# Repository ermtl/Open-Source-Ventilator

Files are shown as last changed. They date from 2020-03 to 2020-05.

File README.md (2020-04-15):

# Open-Source-Ventilator

The project now contains a complete functional ventilator (prototype stage) with both the controller, and the complete mechanical design, all the 3D printed parts (both STL & CAD files) as well as the CNC files for the box.

The complete part list will be updated soon.

Video presentation / demo : 

<a href="http://www.youtube.com/watch?feature=player_embedded&v=0-nGLLX1W8E
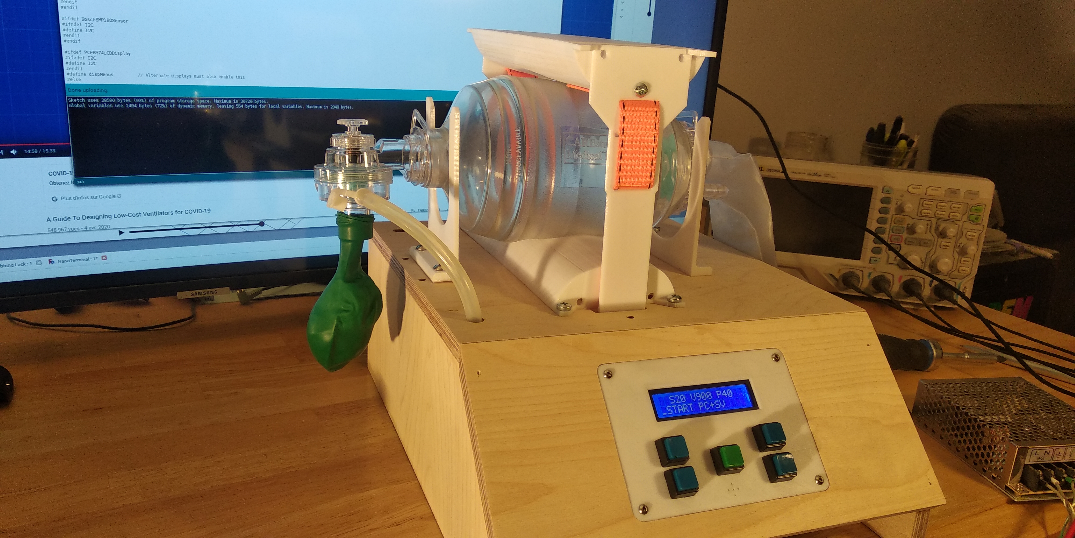
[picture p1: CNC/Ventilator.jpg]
" target="_blank"></a>

The mechanism uses a simple but effective drive mechanism based on a single high strength nylon or polyester webbing strap to squeeze the bag from both sides with minimal mechanical losses.
This design (author unknown) inspired me to explore this solution.

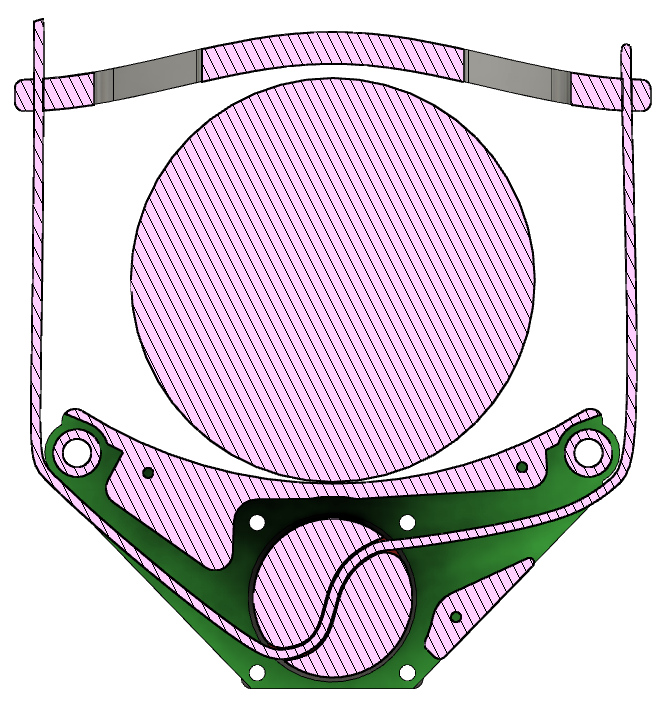
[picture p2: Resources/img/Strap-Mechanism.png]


A major change was to use a much smaller diameter aluminum shaft instead of a drum as this gives the required torque. Also lateral guides are added to ensure a better stability. Also the parts in contact with the BVM are convex instead of being concave as the shape squeezes the BVM in a way that allows to extract more air with minimal force and without damaging the BVM.

The motor is also more powerful than in many other designs I've seen while retaining good position control, allowing it to compress the BVM fast, precisely even at high pressure.

The previously released control software is compatible with this mechanical design and many others.

This software is designed to control a Bag Valve Mask (BVM) AmbuBag medical Ventilator as part of the global effort to develop a fast, effective, easily replicable device using distributed digital manufacturing techniques including 3D printing, CNC or laser cutting. The project uses an Arduino Nano with Atmega328P. The software can be used with a wide range of mechanical designs.

Short video presentation / demo : 

<a href="http://www.youtube.com/watch?feature=player_embedded&v=izh4YnG1fPI
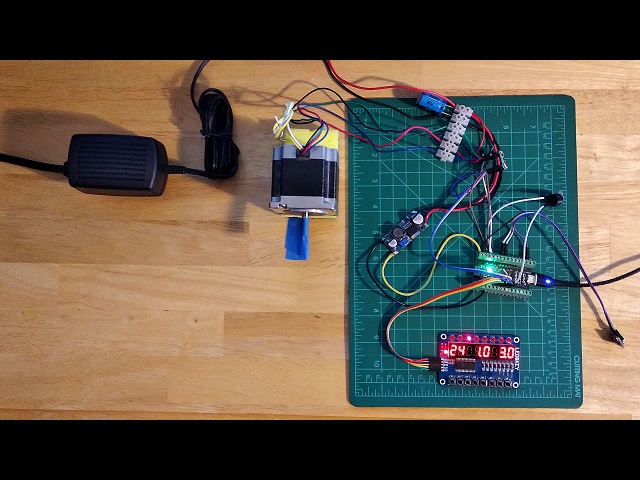
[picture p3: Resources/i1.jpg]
" target="_blank"></a>

(I'm not a youtuber and English's not my main language, you've been warned !)

NOTE: Requirements for a [minimal emergency ventilator device](https://www.gov.uk/government/publications/coronavirus-covid-19-ventilator-supply-specification/rapidly-manufactured-ventilator-system-specification) have been issued by the UK government, and now the WHO as part of a [Disease commodity package](https://www.who.int/publications-detail/disease-commodity-package---novel-coronavirus-(ncov)). This controller strives to follow these guidelines.

Thanks to [uxvrob](https://github.com/uxvrob) we now have a [complete schematic diagram](https://github.com/ermtl/Open-Source-Ventilator/blob/master/hardware/OpenSourceVentilator_sch.pdf) so that the controller can be tested.

As of V0.20, the controller now outputs data that can use an external HMI or the Arduino plotter to output realtime data. Actual plot below (the pink pressure trace was generated by manually pressing an ambu-bag. The right of the screen shows a pressure limited cycle).

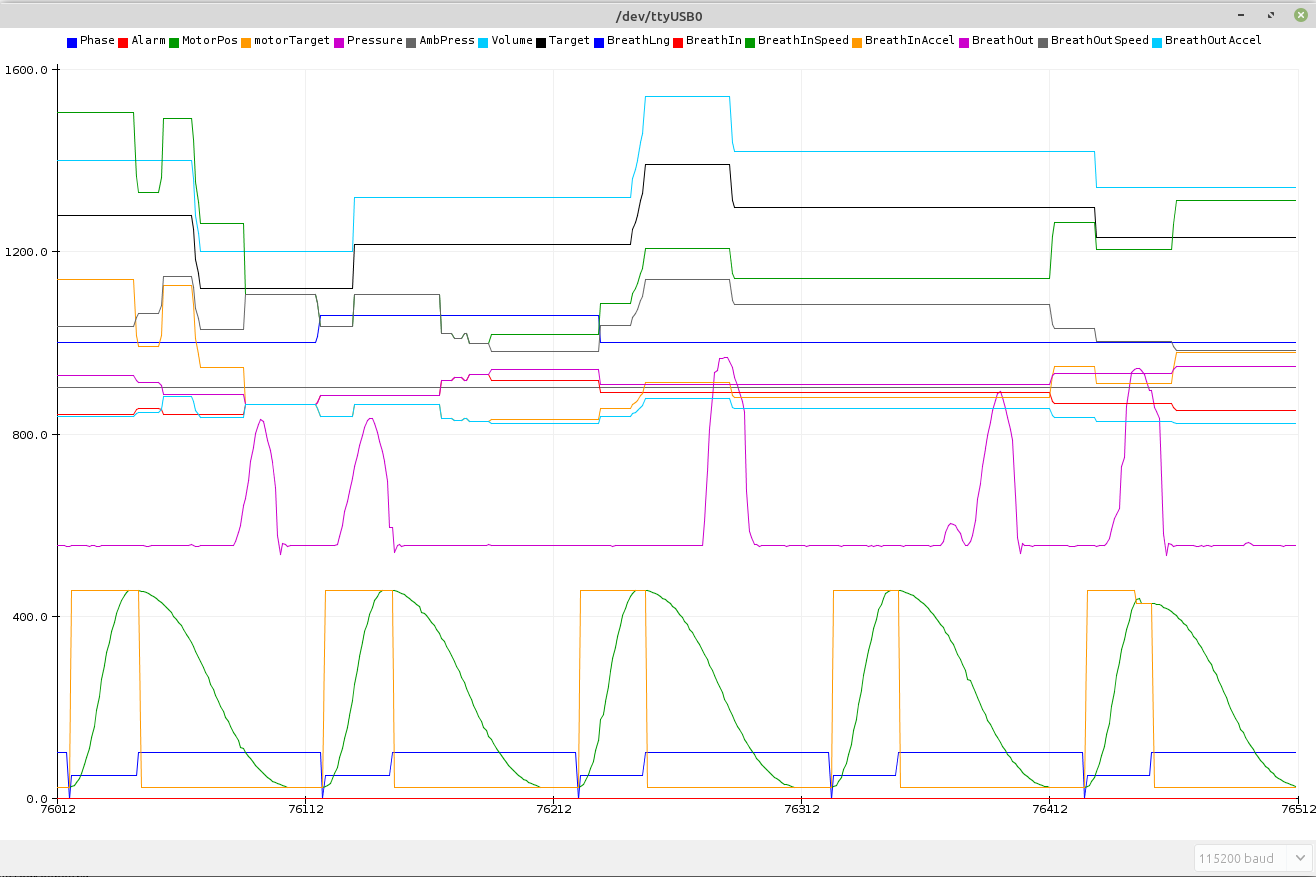
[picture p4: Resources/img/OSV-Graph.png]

 
 (release notes are at the end)

# Main components

- The arduino Nano was chosen as a controller for it's ability to perform the realtime tasks with relatively low latency (step generation & data acquisition) and it's universal availability. More sophisticated controllers such as the Raspberry Pi usually have real time issues and unpredictable latency. Also, the Arduino ecosystem is very rich in well tested libraries.

- The Bosch Sensortech BME280 / BMP280 sensor allows precise measurement of the air pressure delivered to the patient. It also allows measurement of the temperature and pressure (BME280 only). The software allows to use either of these. It'a a well known, mass produced, low cost sensor. 
https://www.bosch-sensortec.com/products/environmental-sensors/humidity-sensors-bme280/

- The TM1638 display / LED / keyboard
This little board merges leds, a 8 digits 7 segments display and 8 buttons. It's a very common Chinese board that possesses numerous advantages. It's main drawback is the Old School look of it's display, but does it really matter for this usage ?
The main advantages are that the board is mechanically integrated making mechanical assembly very easy. Connection to the processor uses only 3 pins (Data, Clock, Strobe) The data is clocked and not timing sensitive. The whole board typically costs 1.50$
2x16 character LCDs require a lot of pin connections or, when used with a "backpack", they require a serial interface. Also, the LCD needs a temperature dependant analog adjustment to be well readable. The display is not very bright and can't be read from a distance. That could be a problem when a person has to monitor several heavily infected patients. They also require a separate keyboard. OLED displays are not suited for this device as their active lifetime is limited. color LCDs would be another possibility, possibly with a touchscreen, but it would take longer to develop and require a more powerful processor without adding much to the main function of the device.

- StepStick stepper driver
The stepstick stepper motor drivers are widely available as they are used to drive 3D printer motors.
When used with 24V and a low current/high torque NEMA23 motor, they can offer a very good torque. There are several types depending on the chip they use (A4988 / DRV8825 / Trinamic TMC2209 & TMC5160). The TMC5160 drives up to 4.4Amps and is even suitable for a NEMA24 or NEMA34 motor. All Trinamic drivers include advanced functions such as load  measurement, stall prevention and detection, noiseless operation, etc ...
https://www.trinamic.com/products/integrated-circuits/
Since the software uses industry standard STEP/DIR interface, any external driver may be used to control a stepper, a servo-stepper or a 3 phases servo. A servo would probably be required for a leadscrew design, while a stepper would be more suited to a direct drive design.

To compile the software, you will need the following libraries (all from the library manager) :
```
#include <BME280I2C.h>             // Temperature / humidity / pressure
                                   //  by Tyler Glenn - https://github.com/finitespace/BME280
#include <Wire.h>                  // I2C protocol
#include <EEPROM.h>                // read / write to the processor's internal EEPROM
#include <TM1638plus.h>            // Keyboard / display / LED combo board
                                   //  By Gavin Lyons - https://github.com/gavinlyonsrepo/TM1638plus
#include <AccelStepper.h>          // Stepper / servo library with step pulse / dir interface
                                   //  By Mike McCauley - http://www.airspayce.com/mikem/arduino/AccelStepper
#include "TimerOne.h"              // Timer component
                                   //  By Jesse Tane, Jérôme Despatis, Michael Polli, Dan Clemens, Paul Stroffregen
                                   //  https://playground.arduino.cc/Code/Timer1/
#include <LiquidCrystal_PCF8574.h> // LCD with PCF8574 "backpack"
                                   //  Matthias Hertel - http://www.mathertel.de/Arduino/LiquidCrystal_PCF8574.aspx 
```
# Software Functions

The software is contained in an Arduino "sketch" with many comments, nearly all parameters are in defined constants and can be easily changed. It is herein distributed under the GPL V3.0 licence. The software has the following functions:

- Initialisation with display keyboard and sensor detection.
The software have been designed to allow operation in degraded mode without BME/BMP280 sensor and even without keyboard / display (it will autostart with stored parameters)
During the startup process, detailed debug information is provided through the serial/USB port. 
TBD : remote operation controlled by USB

- User interface
The software manages the display, keyboard navigation in the settings menu and an alarm beeper.
The 8 leds above the keyboard are used as a bar-graph of the measured pressure and a breath cycle indicator.
The 3rd LED represent neutral atmospheric pressure and blinks at the start of each breathing cycle. 1st and 2nd LEDs on the left indicate a low pressure, those on the right indicate a higher pressure. Display is scaled according to the preset pressure.
The menu allows to change the following parameters:

 - Pulse rate
 The pulse rate in breathing cycles per second can be adjusted between 5 and 60 BPM.

 - Breathing volume
 The breathing volume in liter per cycle can be adjusted between 0.1l and 2l. The motor travel and acceleration are changed according to this parameter. There is a yet to be determined limit for high volume at high pulse rate depending on the mechanical design.
 
 - Breathing Pressure 
 The breathing pressure in KPa can be adjusted between 3Kpa and 30Kpa.
The pressure is used to limit the motor speed / travel to prevent exceeding the preset value.
TBD : This feature is not fully implemented yet (but measurements are available and the stepper library allows to alter the motor parameters while it's rotating).
 
 - Save settings
This saves the 3 settings above  and the running state, thus allowing for automatic start upon powerup.

The user interface management is done in a timed interrupt to be responsive and remain functionnal at all times, so that all parameters can be visualised and changed while the device is operating.

When changing the settings, the change will be gradual with each subsequent breath cycle to prevent sudden changes. The variation speed can be defined for all parameters.

- data acquisition.
Data is acquired from the BME/BMP280 sensor every 100ms. the acquisition includes filtering of the pressure 

# Schematic 

<object data="OpenSourceVentilator/OpenSourceVentilator_sch.pdf" type="application/pdf" width="50%" height="50%">
<embed src="OpenSourceVentilator/OpenSourceVentilator_sch.pdf">
<p>This browser does not support PDFs. Please download the PDF to view it: <a href="OpenSourceVentilator/OpenSourceVentilator_sch.pdf">"Download Schematic</a></p> 
</embed>
</object>

# Required hardware

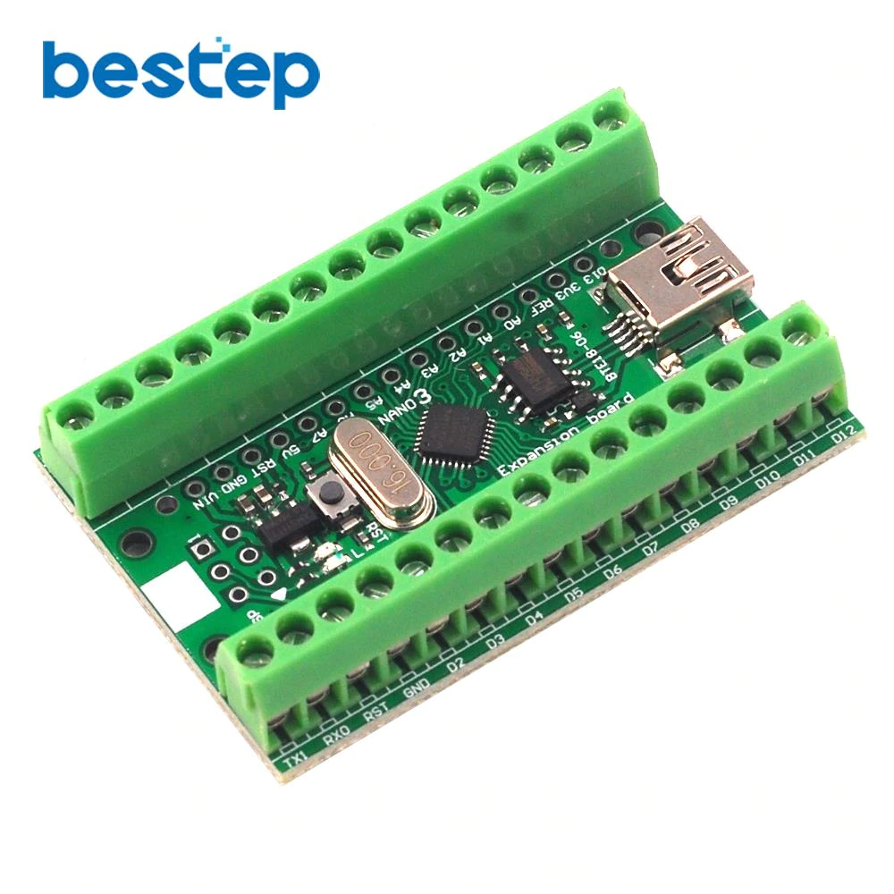
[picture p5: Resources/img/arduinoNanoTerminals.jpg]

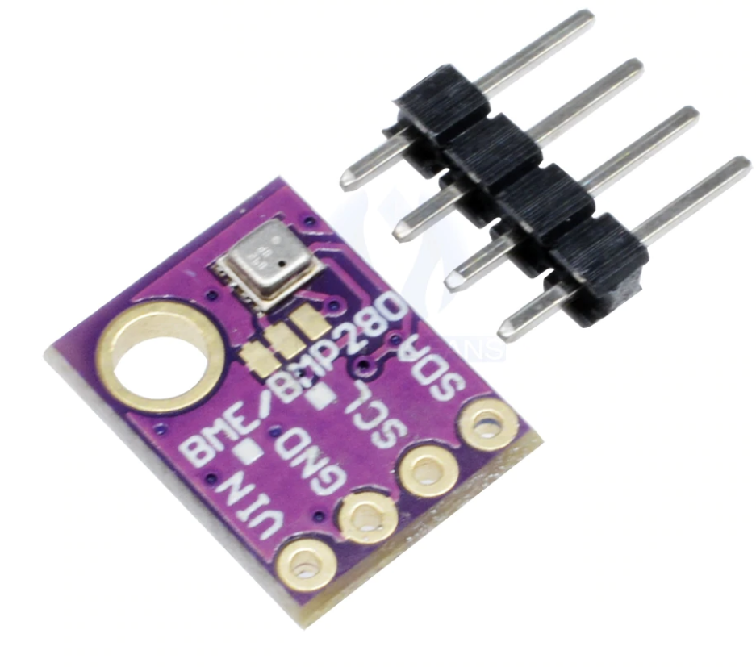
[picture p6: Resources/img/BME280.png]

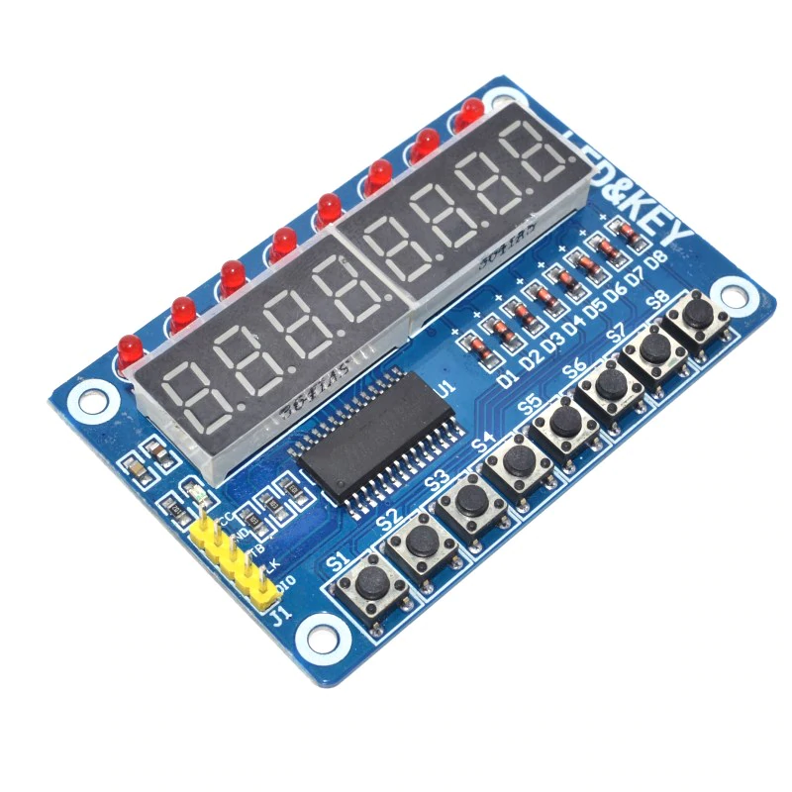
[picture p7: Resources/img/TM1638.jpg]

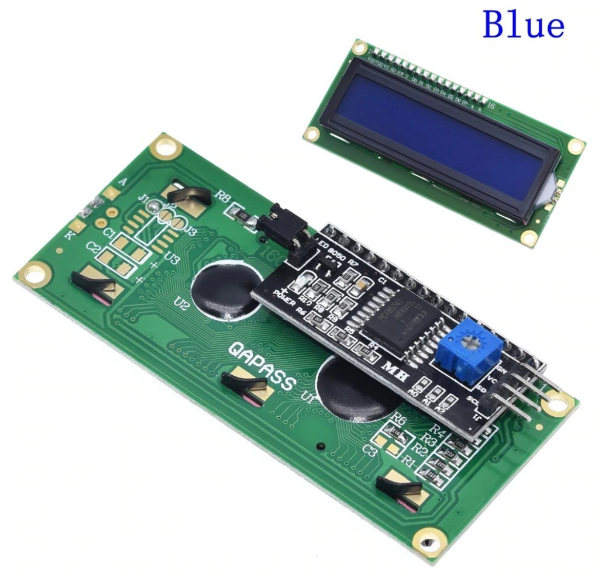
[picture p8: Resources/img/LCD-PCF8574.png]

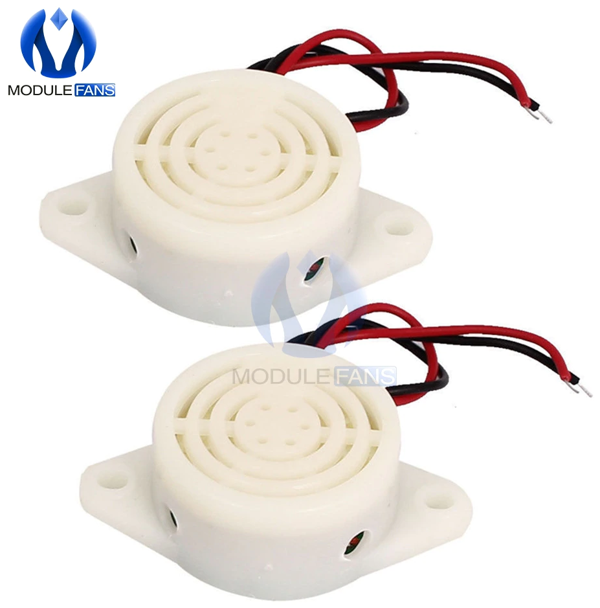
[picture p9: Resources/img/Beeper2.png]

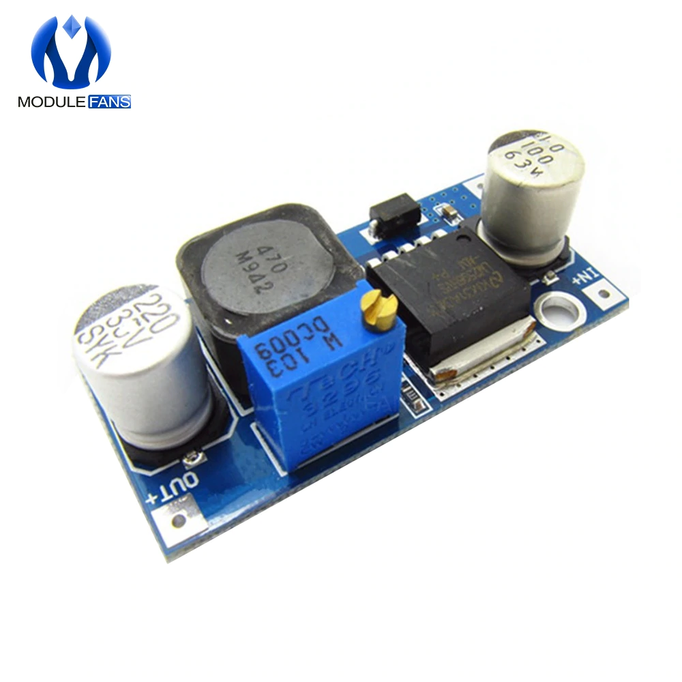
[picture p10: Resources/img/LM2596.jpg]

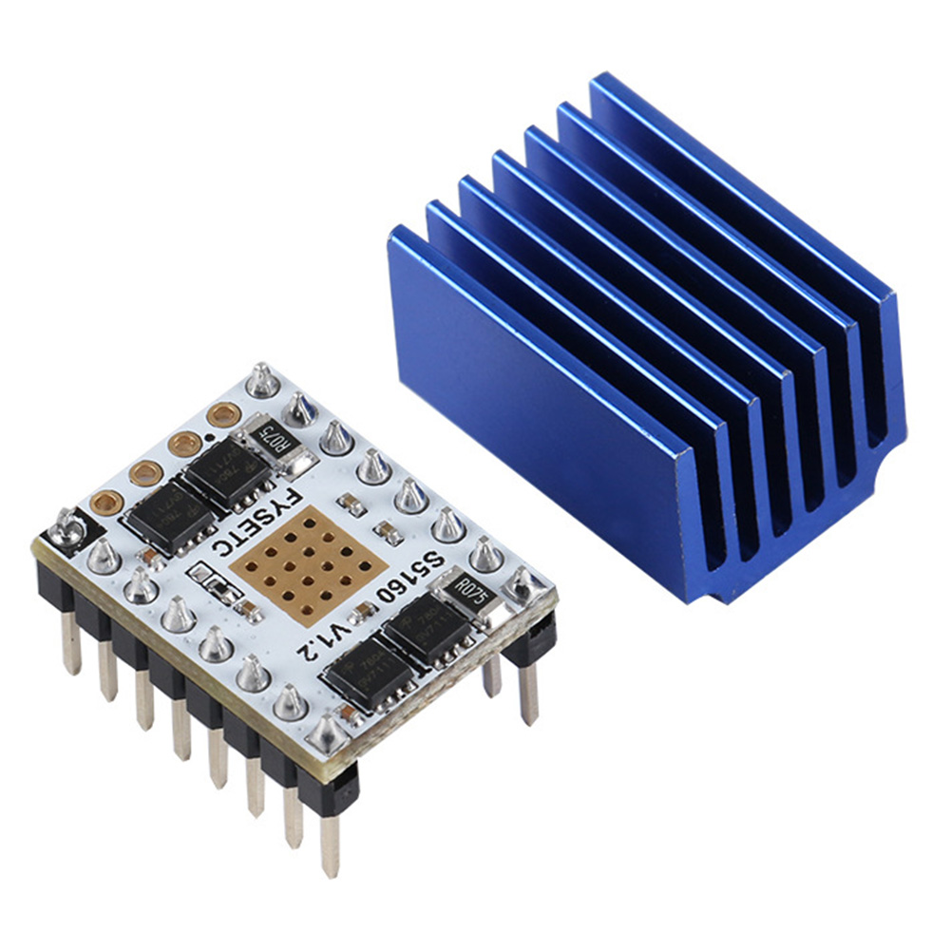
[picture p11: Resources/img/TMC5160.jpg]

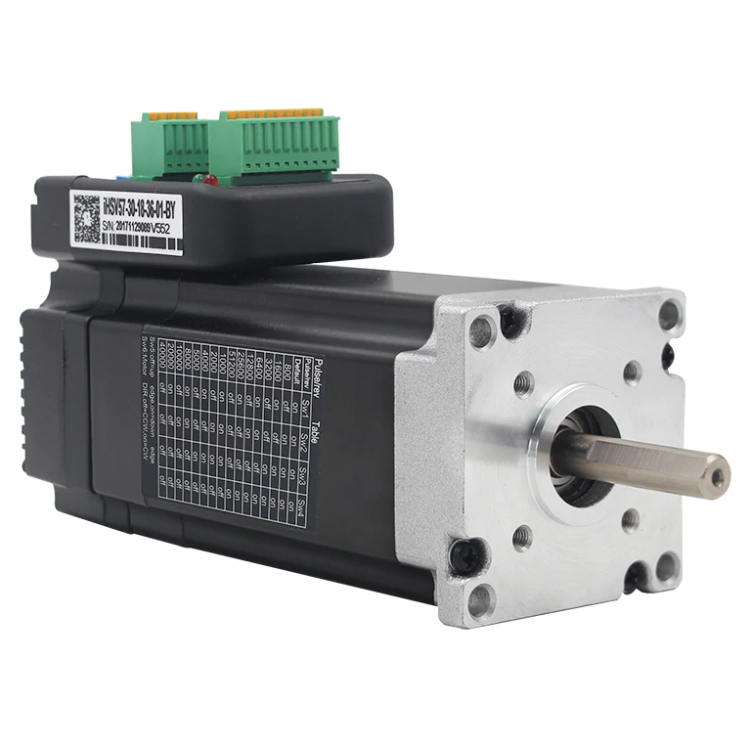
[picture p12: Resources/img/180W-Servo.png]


- Arduino Nano
  Any arduino Nano or clone can be used, as long as it contains an Atmega328 processor
  https://www.aliexpress.com/item/32845440152.html
- Bosch Sensortech BME280 / BMP280 sensor breakout
  Warning, there are 3.3V breakout and 5V breakout boards. Some have 4 pins, others 6 pins.
  They can all be used. Connect the supply accordingly, the 2 extra pins are unused (SPI)
  https://www.aliexpress.com/item/32672562548.html
- TM1638 Display / Leds / Keyboard combo module
  They all have the pin header on top, you can remove the plastic part and bend the pin for side connection
  There are other types of boards with TM1638 chip with 16 buttons, but they lack the LEDs that are important to monitor air pressure measurement.
  https://www.aliexpress.com/item/32807348409.html
- HD44780 With PCF8574 2 lines x 16 character LCD with I2C interface
  These are standard LCD display, and the I2C interface (PCF8574) allows them to be used without taking up many I/O pins.
  https://www.aliexpress.com/item/32651314933.html
- Beeper
  This active beeper is easy to drive and the sound level is mild. 
  https://www.aliexpress.com/item/1893768547.html
  Here is a louder one.
  https://www.aliexpress.com/item/32671465979.html
- Regulator
  Even at 12V, the motor can generate spikes that will damage the controller's regulator. 
  These regulators are cheap, and rated for high voltage (max 50V). 
  The potentiometer needs to be adjusted for 7.5V to 8V
  https://www.aliexpress.com/item/1859113573.html
- Driver and motor.
  The driver and motor required will depend on the mechanical design used.
  here are a few :
  Cheapest, but rugged A4988 Stepstick:
  https://www.aliexpress.com/item/1851964212.html
  DRV8825 StepStick
  https://www.aliexpress.com/item/1937880897.html
  TMC2209 StepStick (silent, with torque detection). 
  Could approximate a pressure measurement for a setup without pressure sensor.
  https://www.aliexpress.com/item/33029587820.html
  TMC5160 StepStick (by far the best option, 4.4A/phase, can drive NEMA34 steppers)
  https://www.aliexpress.com/item/33051621409.html
  As latest calculations ans experimental setups indicate the need for a more powerful
  motor, a LeadShine DM542S (50V 5A seems necessary.
  https://www.aliexpress.com/item/32953743944.html

  For direct drive, a large Nema23 motor with low current and high torque would be best. 
  these motors quickly lose torque as their speed increases, but in this application, 
  their performance should be a good match.
  This one is rated for 1.9NM with only 2.12A (bipolar mode)
  https://www.aliexpress.com/item/4000032106569.html

  For designs using a ballscrew, a servomotor is required to get the necessary speed.
  Here is a good, not too expensive option with integrated controller:
  180W 3000 RPM version https://www.aliexpress.com/item/4000333220649.html
  100W 3000 RPM version https://www.aliexpress.com/item/32945533935.html

# versions

  - 0.10 Initial public version
  
  - 0.11 Add interactive terminal command line complete control (through USB link)
         A minimal device without screen or keyboard is possible with the same software.

  - 0.12 Add "Assist Control" mode with adaptive negative pressure trigger cycle.
This mode was requested by a MD : ```"ER doc here chiming in, hopefully I can answers some questions or clarify minimal requirements.The basic mode you need is Assist Control. This mode provides a breath whenever the patient triggers a breath (by inhaling and creating negative pressure past a certain threshold) or whenever the patient is due for a breath (based on the set rate). The breath it provides are either a fixed volume (and the doc monitors the pressures delivered) or a fixed pressure (and the doc monitors the volume delivered). AC/volume is often called Volume Control, and AC/pressure is often called Pressure Control. While I do not have direct experience ventilating COVID patients yet, these 2 modes will cover 99% of ICU cases."``` 
This version also adds editing, permanent storage and USB setting of the new Patient Synchronization parameter and an audible alarm when pressure remains above 120% of preset pressure for 1 second or mode.
         
  - V0.13 Modular code - asymmetric breathing - Bug fix
This version is a major reorganization of the code done to get a more modular software, ready for bringing in other sensors, a different user interface and ports to other controller architectures. Very long functions are broken down into smaller functionnal blocks that should be much easier to understand and modify, each global variable is commented.
This version also implements most of the guidelines in the UK [minimal emergency ventilator device](https://www.gov.uk/government/publications/coronavirus-covid-19-ventilator-supply-specification/rapidly-manufactured-ventilator-system-specification) specifications. Namely, all variable limits have been tweaked and the variable Inspiratory:Expiratory ratio is fully functionnal.
A bug that allowed floating point variables retrieved from a garbage filled EEPROM to bypass the checks leading to malfunction have been corrected (NaN detection).

  - 0.14 This version include proper timing, speed and acceleration for the motor control.
         The pressure controlled and volume controlled modes are implemented.
         
  - 0.15 Minor version change.
         This version allows the replacement of the buggy Wire.h arduino library  (can hang
         the controller) with a correct version known as jm_Wire
         https://github.com/ermtl/Open-Source-Ventilator/blob/master/OpenSourceVentilator/README.md
         'Wire.h' is still the default library to prevent compiler errors.
         The processor's hardware watchdog can now be enabled (off by default, use with care, you
         risk bricking your processor. 
         Modularisation is getting better (work in progress)         
   
  - 0.16 Double pressure sensor, breath phases modularization
         This version can use 2 absolute sensors (or still use just 1, configurable) to
         constantly monitor the ambiant air pressure. This is important for patients that 
         are heliported and for patients placed in a negative pressure room, 2 situations
         where the ambiant pressure can change rapidly.
         The 2 sensors together will behave as a differential pressure sensor.
         Since pressure is a critical data, several safeguards and coping strategies have 
         been added to make sure data from the sensor is acurate and there is a failsafe.
         Things such as randomly connecting/disconnecting sensors are non blocking and behave 
         as expected.
         this feature requires the #define jm_Wire to be uncommented.Please see the link in
         the description for version 0.15 above

         Also, as requested, the various phases and functions managing the breathing cycle 
         itself have been modularized to allow third parties to implement more sophisticated
         control strategies.

         Finally, the processor's program memory is filing up quickly as the control becomes 
         more complex. There is still opportunities for important optimizations, but the base 
         version will have to give up some non essential functions to fit in a regular Arduino
         Nano (such as the verbose serial interface or the ability to manage both the native
         keyboard / display and the USB serial command line interface.

         This version barely fits with the USB commands on, so they've been deactivated.
         You can get them back by uncommenting the #define USBcontrol line.

         The following versions will both target the Nano and the Mega with Atmega2560 processor
         for 8 times the available program memory.
 
 - 0.17 2x16 LCD Display - Telemetry
       
         The ability to use an alphanumeric 2 lines * 16 characters LCD display had been
         requested, it will now be fully supported. Since this LCD uses lots of IO pins, 
         the retained version is connected to a PCF8574 "Backpack" board to make it I2C 
         compatible. The LCD+the backpack are sold online for around 2.50$.
         The TM1638 display is still supported as a minimal option.
         A good side effect is that the library is lean and so USB/serial terminal control
         is back by default.
         At this point, the keyboard and bargraph are still done with the TM1638, but a
         simple button keyboard will be supported very soon.
         Telemetry will send information in real time about the breathing cycle for further 
         data analysis and / or graphical display !
         This will be very very useful for people developing mechanical solutions, and 
         doing data analysis to develop motor position <=> volume mapping
         Data is sent in common CSV format, around 1 data point every 20 millisecond
         The "T" command, sent through the serial port toggles telemetry on or off.

         every data point includes :
         - Time since the breathing was activated.
         - Breathing cycle phase (more phases might be added in the future)
           0 : Start of new cycle
           1 : Inspiration
           2 : Start of expiration
           3 : Expiration
           4 : Patient breathing initiation search
           5 : Patient initiated a breathing cycle
          - Motor position (in step) Travelled distance depends on driver microstepping
                                     and driving mechanism.
          - relative pressure in cm H2O
         
         In addition to these data points, during phase 0 (start of cycle), the following 
          cycle data is sent:
          - Ambiant pressure (mBar)
          - Breathing volume per cycle in ml
          - Motor destination / target (steps)
          - Breathing length (in seconds)
          - Breathing in duration (in seconds)
          - breathing in top speed (in steps/second)
          - Motor acceleration during inspiration (in steps per second squared)
          - Breathing out duration (in seconds)
          - breathing out top speed (in steps/second)
          - Motor acceleration during expiration (in steps per second squared)
          
    0.20 Realtime graphics, Keyboard, trajectory
         
         This version adds realtime graphics, compatible with the Arduino serial plotter.
         This is an extension of the telemetry in Version 0.17, completed and scaled properly
         for display.
         It shows 2 series of values. The first is updated in realtime (every 20ms) and shows 
         the breathing cycle itself, the commanded motor position, it's actual movement, the 
         pressure sensor output and alarm number.
         The second set is updated once per cycle and shows various values linked to timing, 
         speed, acceleration for various parts of the cycle.
         This data should be extremely useful for developping mechanical prototypes and shows
         the ability to use a remote HMI if desired.
         define ArduinoPlotter for proper visualisation scaling, comment it for real telemetry data 
         This version also add a keyboard as an alternative to the TM1638 keyboard.
         The keyboard used is made with 5 buttons all connected to a single analog input for
         simpler cabling and preserving controller pins.
         https://electronics.stackexchange.com/questions/101409/how-to-debouce-six-buttons-on-one-analog-pin-with-arduino
         The keyboard I use have the following values:
         - 10K to ground
         - 'Enter' button connected to +5V
         - 'Prev'  button connected with a 22Ko resistor
         - 'Next'  button connected with a 10Ko resistor
         - 'Up'    button connected with a 3.6Ko resistor
         - 'Down'  button connected with a 1Ko resistor
         The resulting analog values are stored in the KbdVals[] array, and value tolerance in KbdTols[] array
         If you use different resistor values, uncomment debugAnalogKeyboard to get the analog values to fill the 
         array values.
         Please note that when plotting the graph, while the controller would accept serial data input,the arduino plotter 
         does not allow it, so data needs to be changed using the physical keyboard.
         A 3D printed faceplate containing the display, the buttons and the buzzer is available (including FreeCAD drawing)
         in the 3D-Print directory .
         While graphing the data, a few corrections were made to the trajectory engine.    

    0.21 Pressure unit converted to cm H2O / minor changes
         
         - This version implements the requested change in pressure units as the medical community uses cm H2O and the sensors use Pa.
         - The 'Up' and 'Down' keys now have an auto repeat.
         - When the ventilator is active and 'Enter' is used to stop it, the key press must be pressed 2 seconds and an alarm is sounded.
         - The data dispay includes ambiant pressure (can be used to check negative pressure rooms)
         - It now uses the updated TM1638 library (Version 1.4+), you need to update or you'll have a compile error.
         - #define I2CCheck : displays a list of the I2C devices found upon startup (only for debug or for external HMI)

    0.22 Misc. changes

         - PEEP parameter added
         - Apnea alarm parameter added
         - Display PIP and PEEP in real time (in progress)
         - The bargraph (pressure in VC mode, volume in PC mode) is now displayed on the LCD
         - New automatic motor speed limit to prevent interrupt overflow (interrupt limited reentrancy)
         - reorganisation of items stored in EEPROM. They are now included in a struct and their name starts with ee.
           This will allow easy expansion of the variables stored in EEPROM and the way to treat them as a whole.
         
    0.23 Bug fix with TM1638 display
         When using TM1638 for the display, the menu was broken and displayed an error message.
         
    0.3 Complete ventilator release with plans, 3D prints and CNC 
    
         Complete ventilator release with plans, CAD for 3D prints and CNC
         non linear relation between air volume and motor target position (allows for better adaptation to various non linear   
         mechanisms).
         defining debug_6 allows to check the raw / translated values.
         fix for HD44780 occasionnal display garbling (I2C bus error recovery), requires patched LiquidCrystal_PCF8574 library
         fix for AccelStepper library being too slow to drive microstepped motors, requires patched AccelStepper library
         there is now a separate "OpenSourceVentilator.h" file that contains OEM parameters. 
         This prevents custom changes from being reverted with each new version.
         First version of proportional pressure control  
         Now displays actual volume + actual BPM while breathing
         bug fixes in EEPROM save and restore functions
         bug fix for a mistake that delayed breathing restart
         use of function and unsigned long to prevent millis() rollover problems
         
         thanks to anyone who submitted a bug report!

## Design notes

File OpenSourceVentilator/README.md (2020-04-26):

# Important Note 
about I2C sensors and peripherals using the Arduino Wire.h library

If you compile with any I2C sensor or peripheral that uses the standard Arduino "Wire.h" library, you must be aware that this library is flawed and does contain an infinite loop that will hang the Arduino if an I2C peripheral fails to respond. The only way to exit is to reset it either manually, or using a watchdog. That's been documented since 2011 but Arduino refuses to accept the pull that would correct the situation.

Here are the lines that create the problem (in Wire/utility/twi.c) :

```
// wait for read operation to complete
while(TWI_MRX == twi_state){
continue;
}
```

This case is not supposed to happen according to the I2C protocol, but electrical glitches didn't get the memo. 

Since reliability is paramount in OpenSourceVentilator, the default "Wire.h" library can be switched for the "jm_Wire.h" library that corrects the flaw with a timeout.

However, all libraries that use "Wire.h" will reference it by name in their code, thus a function with the same name will appear to be defined twice, so the compiler will complain loudly and fail.

The solution is to replace the following line in all the library files that contains it.

```
  #include <Wire.h> 
```
with this little preprocessor code
```
  #if __has_include("jm_Wire.h")
  #include <jm_Wire.h>
  #else
  #include <Wire.h>
  #endif
```

That way, the library will use "jm_Wire.h" if it's included in the main program and "Wire.h" otherwise.
You will sometimes need to exit Arduino and restart it for the change to be effective. Unfortunately, if you upgrade a library, you'll have to do the changes all over again. If you know of a better way, please let me know.

here is a list of the libraries used by OpenSourceVentilator and the files that need to be modified:

 - "BME280I2C.h" (pressure / temperature / humidity sensor)
 
   File /libraries/BME280/src/BME280.cpp
 
   File /libraries/BME280/src/BME280I2C.cpp

 - "BMP180MI" (pressure sensor)
 
   File /libraries/BMP180MI/src/BMP180TwoWire.h
   
 - "LiquidCrystal_PCF8574"  (2x16 characters LCD with a PCF8574 "backpack")
 
   File /libraries/LiquidCrystal_PCF8574/src/LiquidCrystal_PCF8574.cpp
 
 - "Adafruit_MPRLS_Library" (pressure sensor)

   File /libraries/Adafruit_MPRLS_Library/Adafruit_MPRLS.cpp

   File /libraries/Adafruit_MPRLS_Library/Adafruit_MPRLS.h

 - "LiquidCrystal_I2C" (various LCD character displays)

   File /libraries/LiquidCrystal_I2C/LiquidCrystal_I2C.cpp
   
   File /libraries/LiquidCrystal_I2C/LiquidCrystal_I2C.h

As I become aware of other libraries used in the project, they will be added to this list.

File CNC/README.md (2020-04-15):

Box-1.DXF contains the plan for cutting the box of the Open Source respirator.
The material to be used is 12mm baltic birch plywood
The plan can be used either as a template for the different parts or to CNC cut the box.

If you use CNC, the source .cb for the [CAD/CAM software CamBam](http://cambam.info/) is included. Cambam is not free software.

Same goes for DriveShaft.cb that shows the slot cutting in the 8mm (5/16") aluminum rod.

<a href="http://www.youtube.com/watch?feature=player_embedded&v=0-nGLLX1W8E
" target="_blank"></a>

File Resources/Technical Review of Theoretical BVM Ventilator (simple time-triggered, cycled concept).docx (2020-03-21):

# TECHNICAL REVIEW:

# Theoretical Bag Valve Mask Ventilator

# 1 Terms and Definitions

Alveolar space – The region of the respiratory system that is composed of elastic, gas-permeable tissue that exchanges gas with the circulatory system.

Airways – The region of the respiratory system that carries gas from the mouth/nose to the alveolar space but does not participate in gas exchange.

Inspiratory time fraction – The portion of the breath time that is provided for inspiration.

Instrumental dead space – The volume of all the breathing system components that carry both inspiratory and expiratory gas.

Peak inspiratory pressure – The maximum airway pressure that occurs during an inspiratory cycle.

Respiratory rate – The number of breaths delivered per unit time.

Tidal volume – The volume inspired or expired in a single breath.

Term | Definition
BVM | Bag valve mask
CO2 | Carbon dioxide
FDA | Food and Drug Administration
O2 | Oxygen

# 2 Theoretical Device Background

The most common manually operated breathing assistance device is the bag mask valve (BVM) which requires manual articulation and the full attention of a medical worker to ensure consistent operation. Additionally, owing to their manual nature, delivery of consistent ventilation is difficult with such devices. The theoretical device would aim to overcome these limitations by providing an automated assisted breathing device that is more accessible than current options and will free medical staff to perform other life-saving tasks. The theoretical device may or may not look something like the following (CRITICAL NOTE: THE PROPOSED THEORETICAL DEVICE WOULD COMPRESS/EXPAND THE BAG BASED ON TIMING ONLY, NOT SENSORS, WHICH EXPLAINS CERTAIN LIMITATIONS DESCRIBED BELOW):

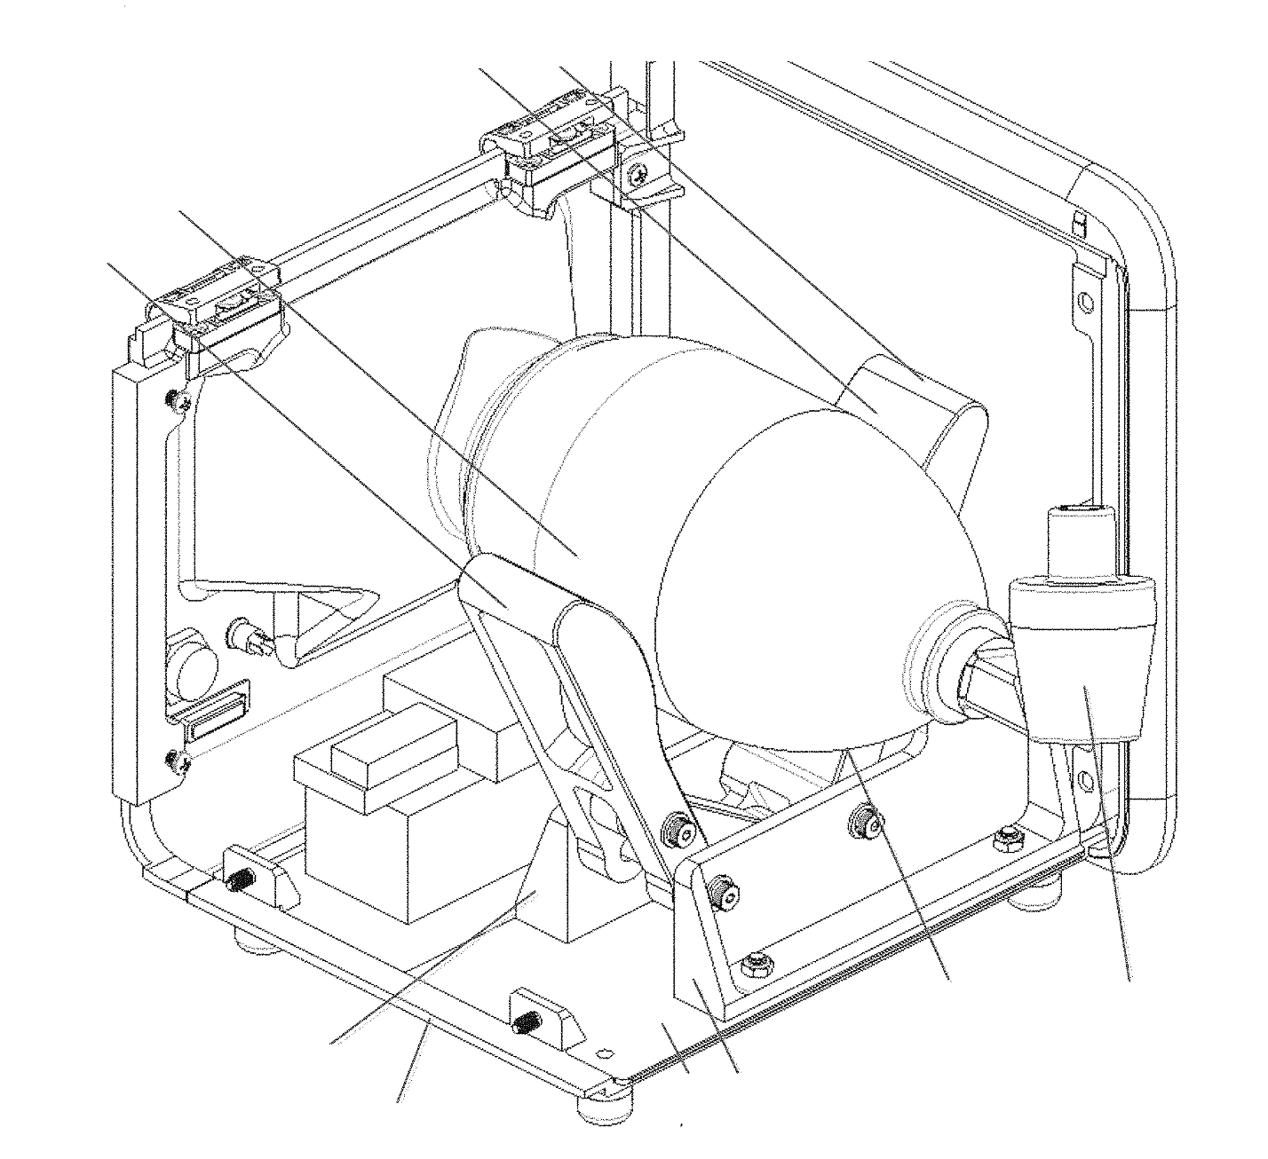
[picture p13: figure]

The target market for this product will be hospitals and medical institutions, particularly in resource limited settings. Additionally, if it is relatively compact and internally powered, the potential product will also be usable in emergency response and during patient transport.

# 3 Key Relevant Standards

The following list represents a selection of key standards that should be reviewed and understood during early product development to help guide the design of the theoretical device. This list, however, is not exhaustive, and compliance with additional standards may be required for regulatory clearance that are either applicable to the specific design, features, or intended use of the product or to medical device development in general.

- IEC 60601-1 – Medical electrical equipment - Part 1: General requirements for basic safety and essential performance.
- IEC 60601-1-2 – Medical electrical equipment - Part 1-2: General requirements for basic safety and essential performance - Collateral Standard: Electromagnetic disturbances - Requirements and tests.
- IEC 60601-1-8 – Medical electrical equipment -- Part 1-8: General requirements for basic safety and essential performance -- Collateral standard: General requirements, tests and guidance for alarm systems in medical electrical equipment and medical electrical systems.
- EN 794-3 – Lung ventilators. Particular requirements for emergency and transport ventilators.
- ISO 10993-1 – Biological evaluation of medical devices -- Part 1: Evaluation and testing within a risk management process.
- IEC 62133 – Secondary cells and batteries containing alkaline or other non-acid electrolytes – Safety requirements for portable sealed secondary cells, and for batteries made from them, for use in portable applications.
- IEC 62304 – Medical device software -- Software life cycle processes.
- IEC 62366-1 – Medical devices -- Part 1: Application of usability engineering to medical devices.

# 4 Technical Review of Limitations of Simple Approach

## 4.1 Bag Valve Mask Overview

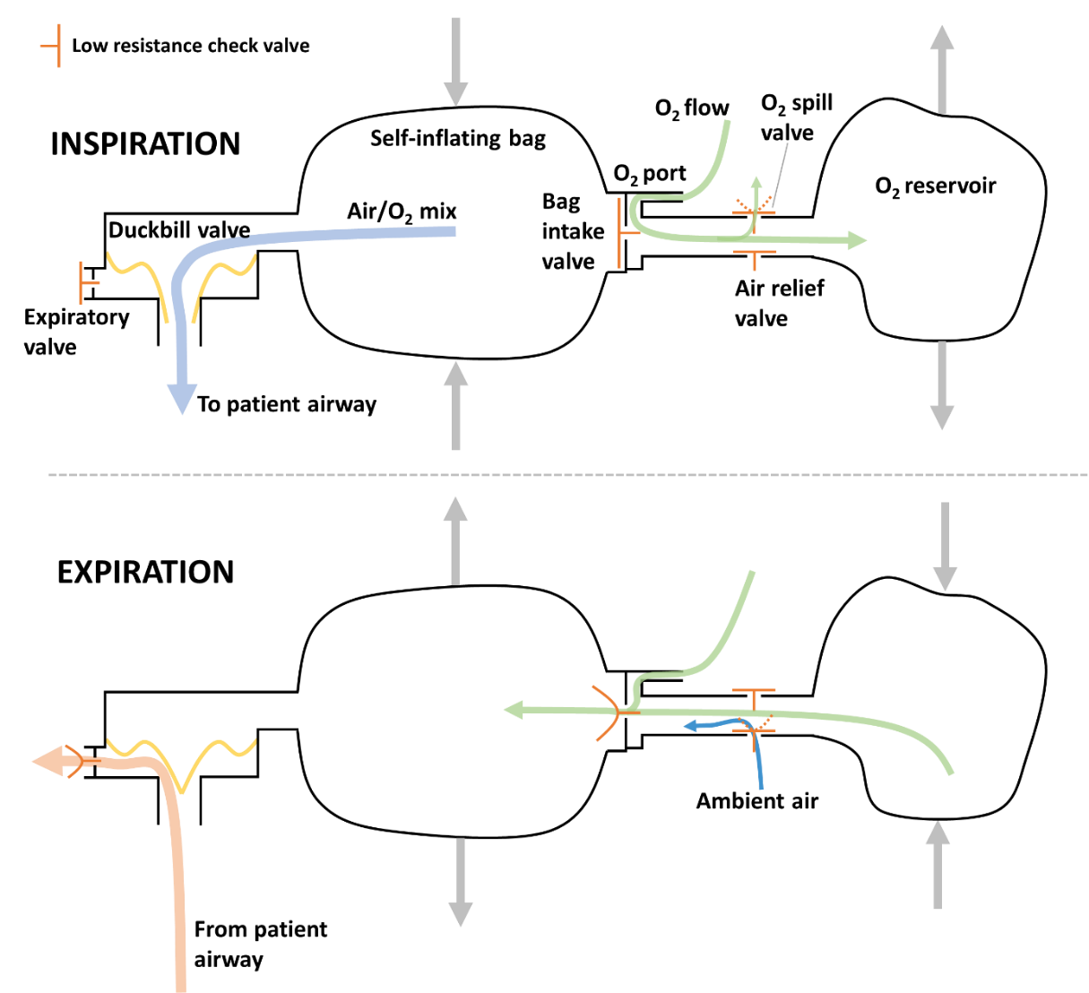
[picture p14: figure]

Figure 1: Schematic representation of a BVM

Figure 1 shows a schematic representation of a typical BVM. During inspiration, the self-inflating bag is compressed, generating a positive internal pressure. The positive pressure forces the bag intake valve closed and deforms the flaps of the duckbill valve to allow delivery of gas to the patient while simultaneously sealing the expiratory port/valve. Low pressure oxygen (O2) delivered through the O2 port is collected in an O2 reservoir; if the reservoir reaches capacity, excess O2 is released through the O2 spill valve.

During expiration, the self-inflating bag recoils to its uncompressed shape, generating a negative internal pressure. The negative pressure pulls the duckbill valve closed and draws O2 into the bag from the O2 reservoir. If the O2 reservoir is emptied, ambient air is entrained via the air relief valve. An annotated photograph of a commercially available BVM is shown in Figure 2.

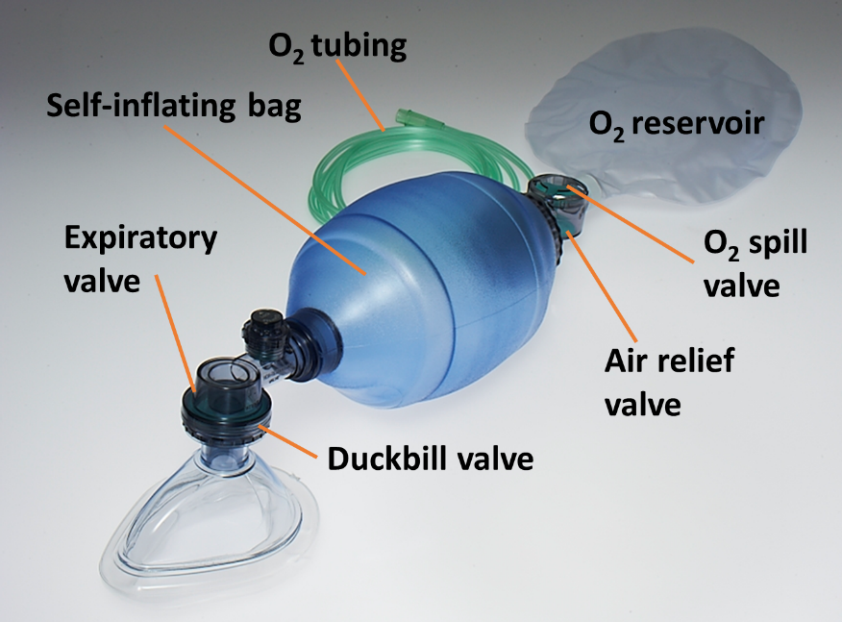
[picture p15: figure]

Figure 2: Commercially available BVM

## 4.2 Dead Space

The role of the respiratory system is to deliver O2 to, and eliminate carbon dioxide (CO2) from, the circulatory system. In the simplest representation, the respiratory system consists of the airways and alveolar space (Figure 3, bottom). During inhalation, fresh gas containing high O2 and no CO2 is drawn, via the airways, into the alveolar space. The alveolar space is composed of highly gas-permeable tissue that is in close communication with the circulatory system. In this space, O2 diffuses from the lungs into the blood and CO2 from the blood into the lungs. During expiration, the low-O2, high-CO2 gas is expelled from the alveolar space via the airways.

The instrumental dead space of a breathing system is the combined volume of all the breathing circuit components that carry both inspiratory and expiratory gas. As shown in Figure 3, any gas that is expired into the dead space of the circuit is subsequently re-inspired without being replaced with fresh inspiratory gas. Over multiple respiratory cycles, the dead space gas is continually depleted of O2, while the CO2 content continually rises. The physiological consequences of the instrumental dead space depend on its size relative to the tidal volume; in the worst case, no fresh gas reaches the alveoli.

For the theoretical device, all the tubing connecting the outlet of the BVM to the patient airway is dead space. Most ventilator systems are set up with approximately 2 m of tubing with 22 mm internal diameter between the ventilator and the patient to facilitate convenient placement of the ventilator and provide a low resistance path for respiration. If this length of tubing was used with the theoretical device, it would contribute 760 ml of dead space to the system. This is well above the average adult tidal volume of 500 ml and, as a result, this configuration of the device would be unable to support life for most patients.

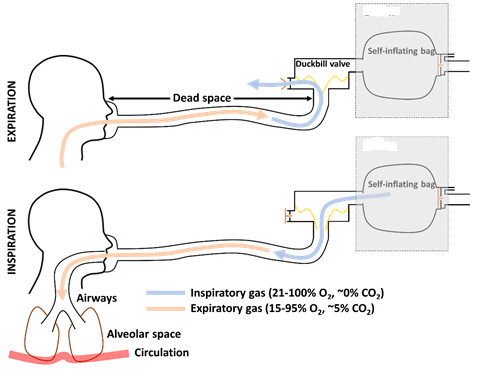
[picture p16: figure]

Figure 3: Theoretical device dead space

In general, it is advisable to limit instrumental dead space to less than 10 ml in adult patients and 5 ml for pediatrics. To maintain the overall “BVM in a box” concept and achieve this significant reduction in dead space, the duckbill/expiratory valve would have to be removed from the BVM and located at the patient airway (Figure 4). In our experience at IPD, this valve is not easily removable from most commercially available BVMs.

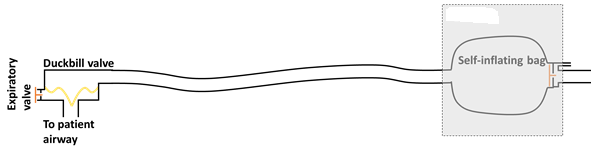
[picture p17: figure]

Figure 4: Theoretical device with reduced dead space

## 4.3 Uncompensated Compliance

When delivering positive pressure ventilation, in any inspiratory cycle, the total volume of gas that enters the lungs is always less than the volume of gas that exits the ventilator. This is a result of two related properties of the system – the compressibility of gas and the compliance of the breathing circuit.

As gas exits the ventilator, and pressure within the system rises, the spacing between gas molecules decreases so that more gas molecules are stored per unit space. At the same time, the increase in pressure causes the ventilator tubing and other parts of the breathing circuit to expand and accommodate more gas compared to the start of inspiration. This gas, which doesn’t reach the patient, is commonly referred to as “lost” to the compliance of the system.

For the theoretical device specifically, the patient tidal volume will be lower than the volumetric compression of the BVM. This effect may be compounded by the significant volume and elastance of the self-inflating bag. As noted in section 4.2, the volume of 2 m of standard ventilator tubing is approximately 760 ml. As the volume of a typical adult BVM is 1500 ml, the total theoretical device breathing system volume is approximately 2260 ml. Similarly, the volumetric expansion of 22 mm ventilator tubing is approximately 0.5 ml/cmH2O/m⁸. Based on a conservative estimate for the BVM compliance of 0.5 ml/cmH2O, the total circuit compliance can be approximated as 1.5 ml/cmH2O.

The gas lost to the system can be calculated according to Equation 1, where VL is the lost volume, and PIP, Patm, VC, and Cc are the peak inspiratory pressure, atmospheric pressure, breathing circuit volume, and breathing circuit compliance, respectively. Using the above approximations for circuit volume and compliance, the percent error in volume delivery can been calculated for a standard adult and pediatric patient⁹ (Table 1).

V_L =((PIP+P_(atm))/(P_(atm))-1)V_C +PIP∙C_c Equation (1)

Table 1: Volumetric error due to circuit compliance

Parameter | Adult | Pediatric
Static lung compliance (ml/cmH2O) | 50 | 20
Airway resistance (cmH2O/L/s) | 5 | 20
Set tidal volume (ml) | 500 | 300
Respiratory rate (breaths/min) | 10 | 20
Inspiratory time fraction | 0.33 | 0.33
PIP (cmH2O) | 11.3 | 21.1
Lost volume (ml) | 41.5 | 77.7
Delivered tidal volume (mL) | 458.5 | 222.3
Error: Delivered vs Target (%) | 8.3 | 25.9

Note: Patm of 1 atm was used in the above calculations

A priori compensation for this error is difficult to implement because, as shown in Table 1, the error depends on the delivered respiratory profile and the respiratory mechanics of the patient. In addition, the error will vary with the volume and compliance of the breathing circuit that is used, which may change between patients. Lastly, the compliance of an individual breathing circuit may change with temperature and over time.

This limitation is overcome in existing ventilators by a number of different techniques. Most commonly, ventilators execute a circuit compliance check before each new patient and then dynamically measure the circuit pressure and correct the delivered volume in real-time throughout inspiration. Other ventilators may incorporate a flow sensor at the patient airway for monitoring the actual delivered tidal volume. Alternatively, most ventilators implement a pressure control mode wherein the ventilator targets a specific airway pressure instead of a tidal volume, and the control loop inherently compensates for any volumetric losses.

## 4.4 Oxygen Delivery

As shown in Figure 1 and Figure 2, BVMs typically incorporate an O2 reservoir to collect O2 during compression of the self-inflating bag which is subsequently drawn into the system as the bag recoils. To achieve >95% O2 in the inspired gas⁹ the O2 reservoir should be large enough to accumulate at least one tidal volume. A bag of roughly 1 L should be sufficient for most patients. Based on IPD’s current understanding and review, the theoretical device does not contemplate the attachment of an O2 reservoir and associated relief valves. While provision of O2 without a reservoir will increase the inspired O2 fraction, the utilization of the supplied O2 will be inferior to the reservoir approach. For example, using a standard adult patient with a tidal volume of 500 ml, respiratory rate of 10 breaths/min, and inspiratory time fraction of 0.33, a flow of 5 L/min of O2 would result in ~100% inspired oxygen fraction with a reservoir; without a reservoir, the inspired oxygen fraction would be 73%. Addition of an O2 reservoir to the current design would require that the reservoir be placed externally, and a means provided to prevent unintentional compression (ex. a cage). Alternatively, the reservoir could be incorporated inside the theoretical device but would likely require an increase in product size to accommodate the additional volume.

## 4.5 Respiratory Rate

The respiratory rate achievable with the theoretical device will be limited by the rate at which the self-inflating bag re-inflates after compression. Although adult respiratory rates (~10 breaths/min) may be easily achievable, pediatric respiratory rates (20+ breaths/min) may be difficult to achieve with an adult sized bag. In normal practise, BVMs are available in various sizes to accommodate adults, pediatrics, and neonates, where the recoil rate of each type of bag is sufficient to achieve the respiratory rates required for the intended patient population. The theoretical device may contemplate the addition of loops and hooks to the bag/compression system to allow for pulling the bag during expiration. Although this solution is viable, it would require a custom BVM to implement.

## 4.6 Variations in Bag Valve Masks

The size and shape of BVMs is not standardized between products. If the theoretical product volume delivery is calibrated to a particular BVM, substitution of the BVM with a product with different geometry could lead to very significant errors in volume delivery. Additionally, the theoretical device structure would need to accommodate BVMs of varying shapes and sizes.

# 5 Considerations for Addressing Limitations

## 5.1 Parameters, Features, and Modes

Although the adjustable parameters, features, and available modes of ventilation differ significantly between ventilators, there is a subset of functionality that is common to many ventilators, including emergency and transport ventilators. The following is a list of some common functions that may be difficult to implement on the proposed theoretical device:

Inspiratory/expiratory timing – Although the theoretical device can vary respiratory rate based on the motor speed, it may be desirable to adjust the portion of the breath time that is allocated to inspiration and expiration separately. This would require sensing and feedback of the position of the compression mechanism to determine when the self-inflating back is being compressed (inspiration) and expanded (expiration), and adjustment of the motor speed during each phase appropriately. If this is not feasible, it is recommended that the device implement the most common inspiratory time to expiratory time ratio of 1:2, respectively. In general, it is unnecessary to control the rate at which the bag re-inflates and may be preferable to have the compression mechanism retract as quickly as possible after inspiration is complete.

Triggering/cycling – Triggering and cycling refer to the criteria for initiating and stopping inspiration, respectively¹⁰. The current concept of the theoretical device is both time-triggered and time-cycled. In many cases, it is beneficial to trigger or cycle a breath based on a patient signal. For example, patients do not always require full ventilatory support and may make weak and/or intermittent efforts to breath spontaneously. In this case, the ventilator may support spontaneous inspiratory efforts by detecting negative airway pressures and triggering a ventilator assisted breath. Similarly, a very high airway pressure during inspiration may indicate that the patient is trying to expire against the ventilator and the breath should be cycled. With the simple theoretical device, the motion of the compression mechanism is fixed. Implementation of any trigger or cycle conditions other than time may be very difficult as these features generally require near instantaneous switching between inspiration and expiration.

Pressure controlled ventilation – Most modern ventilators include a pressure control mode wherein the ventilator delivers a specific airway pressure profile instead of delivering a set tidal volume. Pressure control has many advantages over volume control, including automatic compensation for volume loss (compliance, leaks, etc.) and adjustment to changes in the patient’s respiratory mechanics. This mode, however, generally requires that the airway pressure be sensed and fed back to the ventilator gas source so that the airway pressure adheres to the setpoint. The bag/compression system in the current design may be unable to respond to changes in airway pressure with sufficient speed to implement this mode.

## 5.2 Key Safety Features

The following list provides a high-level summary of some of the most important safety requirements included in standard EN 794-3 (Lung ventilators - Part 3: Particular requirements for emergency and transport ventilators). Although it is not a complete list of all safety requirements, it is intended to highlight some of the most critical safety features to consider during design of the theoretical device. Some of these features may already be incorporated into the BVM, which can be checked by cross-referencing standard ISO 10651-4 (Lung ventilators – Part 4: Particular requirements for operator-powered resuscitators).

- During power failure, the resistance at the patient connection port to inspiratory and expiratory flows shall not exceed 0.6 kPa (6 cmH2O) at 30 l/min for adult use, 0.6 kPa at 15 l/min for paediatric use, and 0.6 kPa at 2.5 l/min for neonatal use.
- The inspiratory and expiratory resistance measured at the patient connection port shall, during spontaneous breathing and normal operation, not exceed 0.6 kPa (6 cmH2O) at 60 l/min for adult use, 30 l/min for paediatric use, and 5 l/min for neonatal use.
- The ventilator shall have a power failure alarm which activates a continuous visual signal or an auditory signal of at least 7 s duration if the internal or external, electrical or pneumatic, power supply falls below the values specified by the manufacturer.
- A high pressure alarm shall be provided. It shall activate an auditory signal when the inspiratory pressure alarm level is reached.
- The system pressure shall be limited to less than 6.6 kPa (66 cmH2O), i.e. 6.0 kPa + 10 % during normal use.
- The maximum achievable pressure at the patient connection port under single fault condition shall not exceed 10 kPa (100 cmH2O).
- Means shall be provided to prevent or indicate hypoventilation due to inadvertent reduction in inspiratory flow.
- An emergency air intake port shall be provided and shall not accept any connector complying with EN 1281-1 and EN 1281-2. The emergency air intake port should be designed so that it cannot easily be obstructed when the ventilator is in use.

# 6 Alternative Concepts

## 6.1 Anesthetic Circle System Ventilator

Inhalational volatile anesthetics are the most commonly used type of anesthetic during surgery. However, they have low solubility in the blood, so most of the anesthetic inhaled by the patient is subsequently exhaled. Anesthetic circle systems are type of ventilator system that are designed to reuse the patient’s exhaled gas to conserve anesthetic. A typical anesthetic circle system is shown in Figure 5 below.

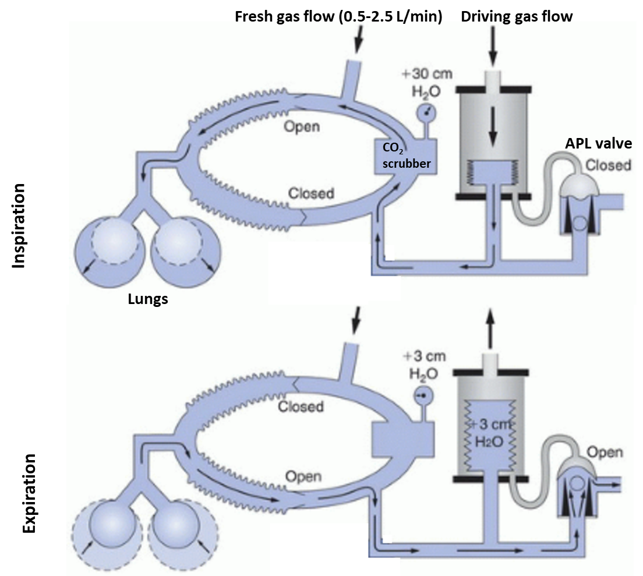
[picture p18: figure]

Figure 5: Anesthetic Circle System

During inspiration, a driving gas flow enters a rigid container with a collapsible bellows, causing the bellows to collapse and deliver gas to the patient. During exhalation, the expired has is directed back into the bellows allowing it to re-inflate.

The APL valve contains a flexible seal that, during inspiration, is forced down by the pressure of the driving gas, sealing the circuit. During expiration, the APL valve is released, allowing any expired gas in excess of the bellows volume to leave the circuit. A slight resistance in the APL valve, represented by the floating ball, ensures that during inspiration the pressure on the topside of the seal is greater than on the bottom side, causing the valve to close; during expiration, the resistance ensures that bellows fills preferentially before expired gas is released from the circuit.

The patient rebreathes previously exhaled gas which, normally, has low O2 content and high CO2 content. This is enabled by two features. Firstly, there is a CO2 scrubber in the circuit which removes CO2 from the expired gas. Secondly, a small flow of high O2 fresh gas is continuously delivered into the circuit which replenishes the oxygen supply, carries the anesthetic, and tops up any volume removed by the scrubber or lost due to leaks in the circuit.

Not shown in Figure 5 is the ventilator controller which sets the rate, flow, and pressure of the driving gas to achieve the desired ventilation profile. Title volume is usually set by either by a movable mechanical stop in the bellows container that limits the maximum height the bellows reaches on inflation or by adjusting the inspiratory time and inspiratory flow.

### 6.1.1 Relevance to the Theoretical Device

The ventilator portion of an anesthetic circle system (bellows, controller) is a fairly simple design, and available from many manufacturers in a variety of sizes with a variety of different features (Figure 6). Starting from one of these platforms may allow you to accelerate development. They often include basic rate and flow/volume controls, in addition to high and low pressure alarms. There are also companies that offer OEM versions of such ventilators¹¹ that would provide a very good base to begin development.

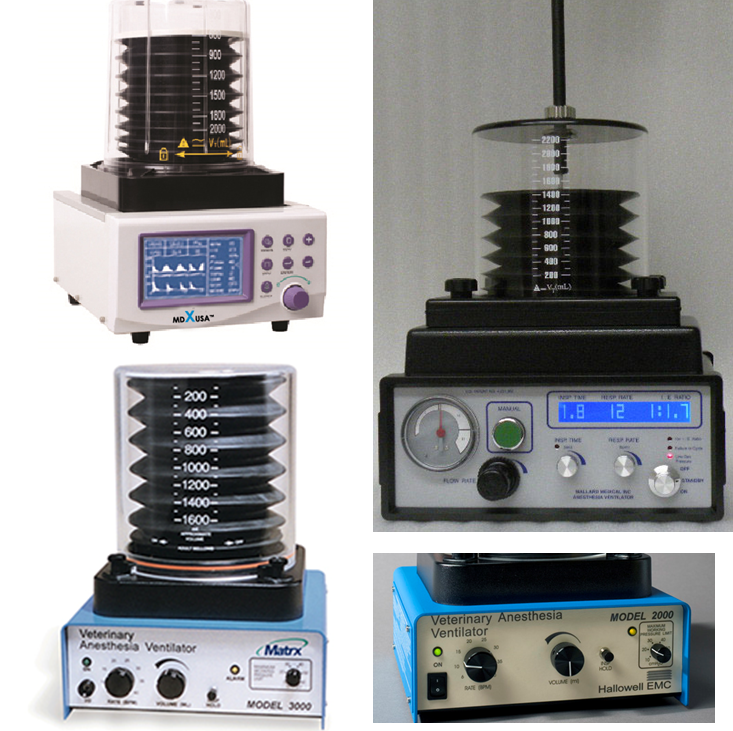
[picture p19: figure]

Figure 6: Various bellows ventilators

### 6.1.2 Challenges and Potential Solutions

The primary challenge with modifying a circle system ventilator is reinflation of the bellows. In the typical use scenario, this is accomplished by the patient’s expired gas with the appropriate scrubbers and fresh gas flows to allow for rebreathing. Without these elements, using a traditional circle system is not feasible. A potential modification to the standard circle system ventilator setup to overcome this challenge is shown in Figure 7 below.

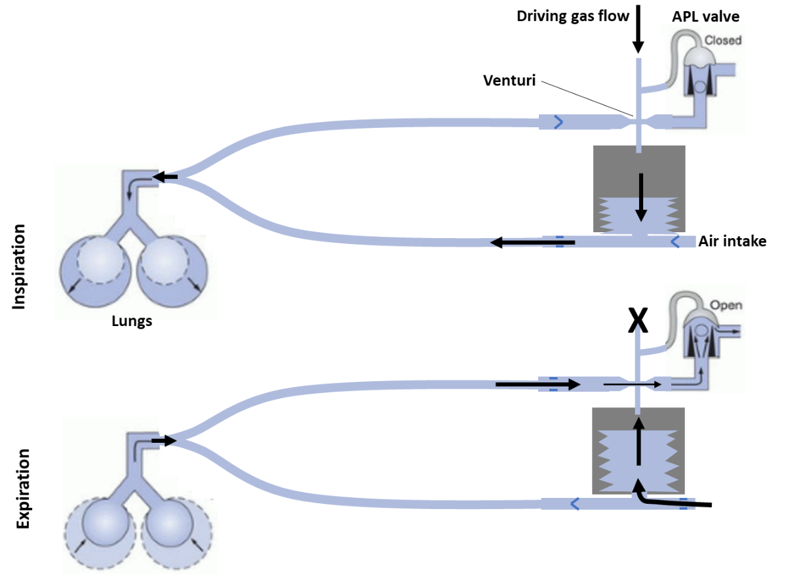
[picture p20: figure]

Figure 7: Modified circle system for bellows reinflation

In this configuration, during inspiration, the flow patterns are the same as the standard configuration – a driving gas compresses the bellows which delivers gas to the patient. During expiration, the driving gas is shut off, the APL valve opens, and the patient exhales out the APL valve through a Venturi tube. As gas passes through the narrow throat section of the Venturi, its velocity increases and, based on conservation of energy, its static pressure decreases. A venturi can be designed so that as gas passes through the throat, the pressure within the throat decreases below the ambient barometric pressure. This forms the basis of the well-known Venturi pump. By connecting the throat section of the Venturi to the bellows container, the patient’s exhaled gas may generate suction which causes the bellows to rise and draw in ambient air for the next inspiratory cycle.

### 6.1.3 Critique

The use of a circle system ventilator may provide a simple platform to begin development of the theoretical device. Many models are available from many manufacturers, including some which supply OEM components. It is also aligned with the “bag-in-a-box” approach. However, circle systems were designed for a specific use case – ventilation during surgery where reuse of the patient’s exhaled gas is important for conserving inhalational anesthetics – and may require significant modification for more general use where a CO2 scrubber and fresh gas flow is not available or desired.

The concept shown in Figure 7 is a potential solution to reinflation of the bellows without rebreathing. It has the advantage that it uses the kinetic energy of the gas molecules in the expiratory flow to provide suction and draw in ambient air, potentially decreasing power consumption and increasing battery life. However, the velocity of exhaled gas may be insufficient to generate enough suction, and experimentation would be required. In addition, any leaks between the patient and Venturi will reduce the flow through the Venturi and reinflation of the bellows.

More obvious solutions to the problem include using a bellows which self-inflates during exhalation (like a BVM); switching the driving gas between the bellows container and air intake port during inspiration and expiration, respectively; or using a reversable source of driving gas that can provide positive pressure and negative pressure to the bellows container during inspiration and expiration, respectively. A mechanical driving force, such as a linear motor, can also be used. These solutions will be more robust, but less power-efficient.

### 6.1.4 Existing Technology

We are currently unaware of any products that use a Venturi tube to reinflate a ventilator bellows, as shown in Figure 7. However, our search was not exhaustive, and should you decide to pursue this idea, we recommend a thorough intellectual property search by a qualified professional.

Other respiratory devices that use the Venturi principle include:

- Venturi oxygen masks (Intersurgical Ltd., 1040090)
- Venturi percussive ventilators (Hill-Rom, MetaNeb)
- Ventilators with Venturi tubes on the inspiratory limb for entrainment/mixing of gases¹²

# 7 References

1. United States Food and Drug Administration. General Controls for Medical Devices. Available at: https://www.fda.gov/MedicalDevices/DeviceRegulationandGuidance/Overview/GeneralandSpecialControls/ucm055910.htm. (Accessed: 25th February 2018)

2. United States Food and Drug Administration. Classify Your Medical Device. Available at: https://www.fda.gov/MedicalDevices/DeviceRegulationandGuidance/Overview/ClassifyYourDevice/ucm2005371.htm. (Accessed: 5th March 2018)

3. United States Code of Federal Regulations. Definitions. 21 CFR §860.3. (2018).

4. United States Food and Drug Administration. FDA and Industry Procedures for Section 513(g) Requests for Information Under the Federal Food, Drug, and Cosmetic Act. Guidance for Industry and Food and Drug Administration Staff. (2012).

5. United States Code of Federal Regulations. Powered emergency ventilator. 21 CFR §868.5925. (2018).

6. United States Food and Drug Administration. The 510(k) Program: Evaluating Substantial Equivalence in Premarket Notifications [510(k)]. Guidance for Industry and Food and Drug Administration Staff. (2014).

7. United States Food and Drug Administration. 510(k) Premarket Notification Database. Available at: https://www.accessdata.fda.gov/scripts/cdrh/cfdocs/cfPMN/pmn.cfm. (Accessed: 20th March 2018)

8. GE Healthcare. Breathing Systems. iBreathe custom configured breathing circuit kits. Doc No: DOC1460178. (2013).

9. European Committee for Standardization. EN 794-3:1998+A2:2009. Lung ventilators - Part 3: Particular requirements for emergency and transport ventilators. (2009).

10. Chatburn, R. L., El-Khatib, M. & Mireles-Cabodevila, E. A taxonomy for mechanical ventilation: 10 fundamental maxims. Respir. Care 59, 1747–63 (2014).

11. Penlon. Original Equipment Supplier. Available at: http://www.penlon.com/en/us/products/oem.html. (Accessed: 16th May 2018)

12. Jain, R. K. & Swaminathan, S. Anaesthesia ventilators. Indian J. Anaesth. 57, 525–32 (2013).

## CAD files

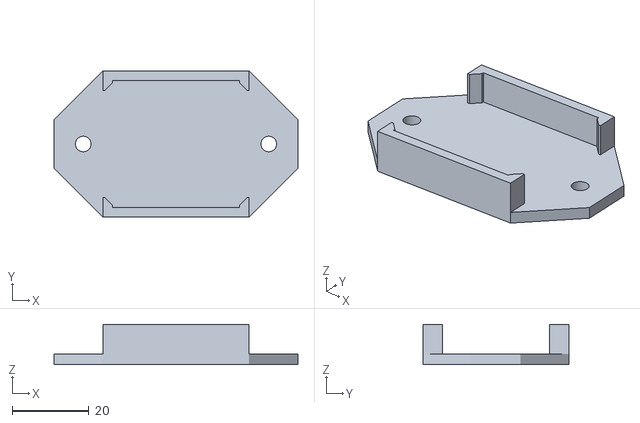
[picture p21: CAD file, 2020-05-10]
3D-Print/Foam Peep 3.stl
63.5 x 38.1 x 10.4

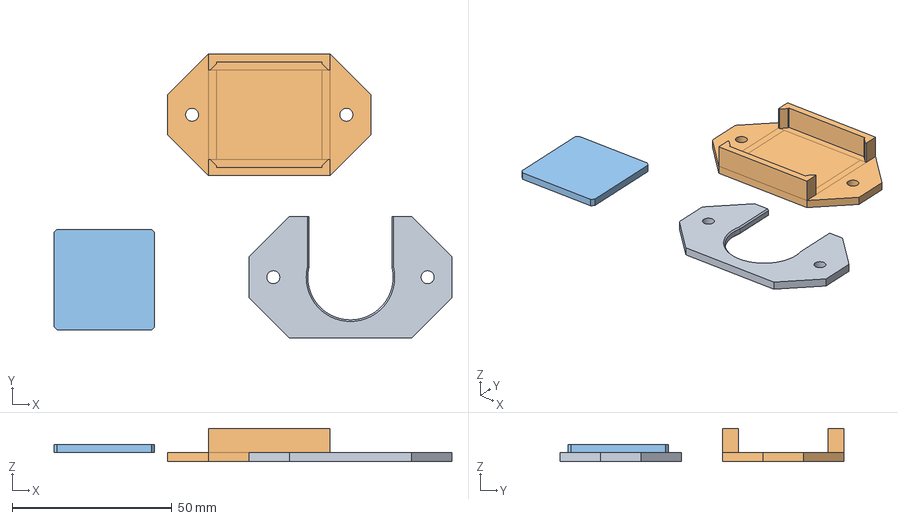
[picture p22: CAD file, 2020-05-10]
3D-Print/Foam Peep Valve.FCStd
124.5 x 88.9 x 10.4 mm

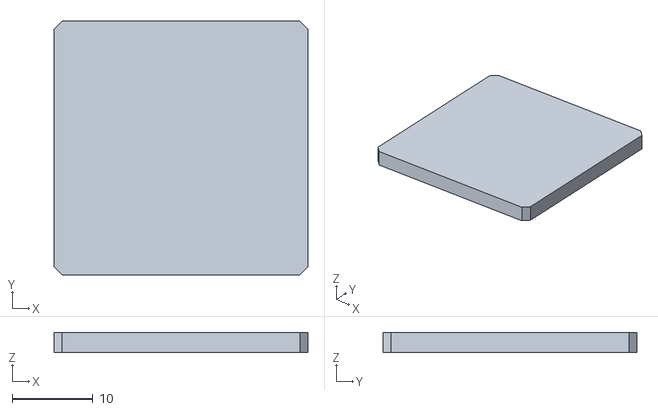
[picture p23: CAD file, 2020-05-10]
3D-Print/Foam Peep 2.stl
31.5 x 31.5 x 2.54

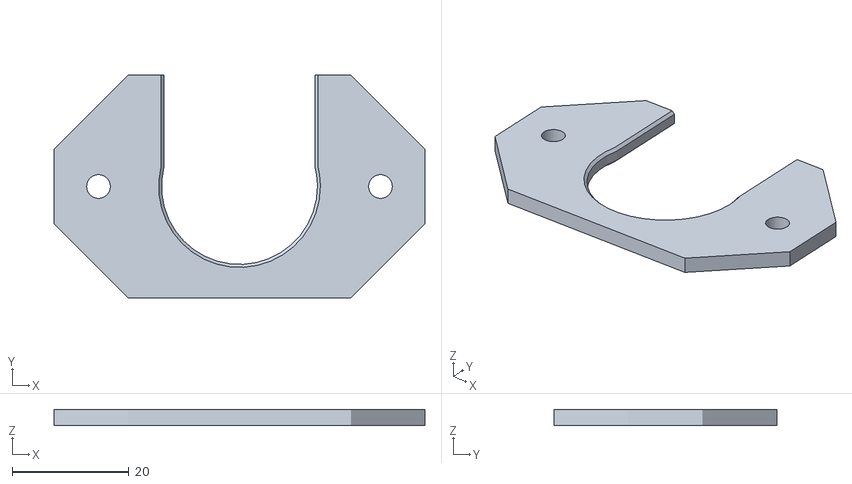
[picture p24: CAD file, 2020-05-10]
3D-Print/Foam Peep 1.stl
63.5 x 38.1 x 2.79

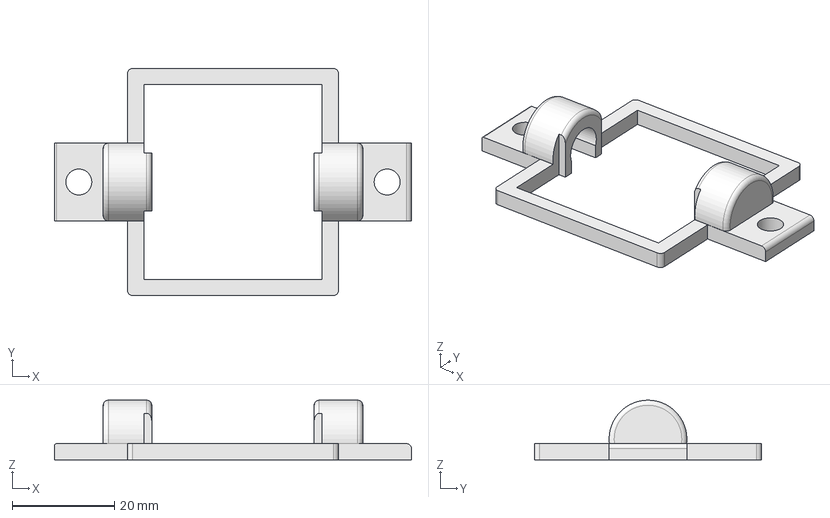
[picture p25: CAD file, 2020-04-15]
3D-Print/RollerHolder.FCStd
69.8 x 44.5 x 11.7 mm

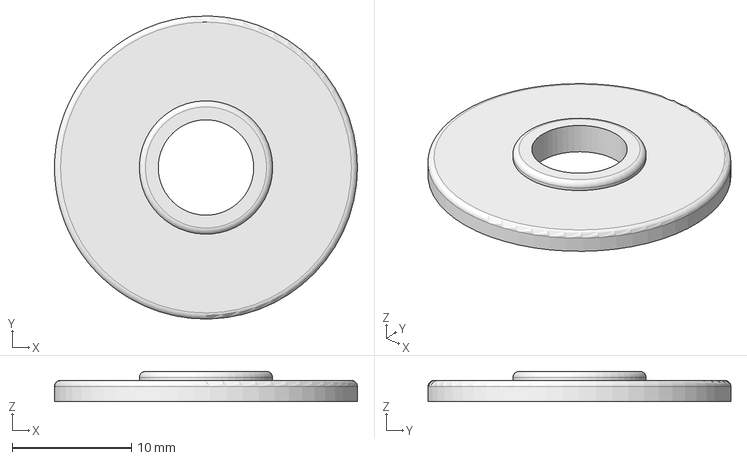
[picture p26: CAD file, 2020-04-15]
3D-Print/BearingFlange.FCStd
25.4 x 25.4 x 2.54 mm

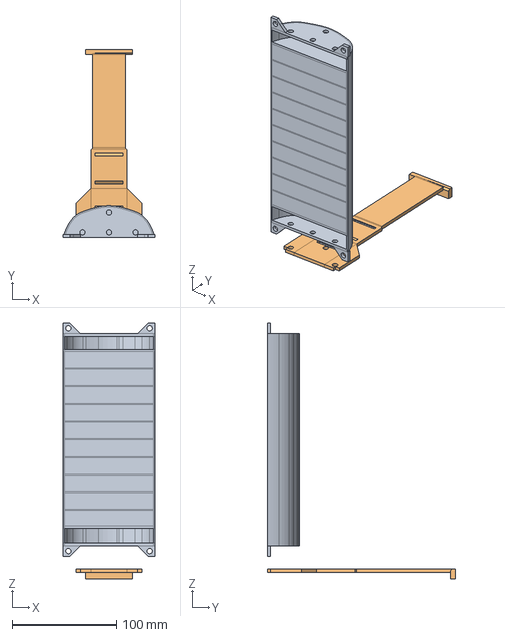
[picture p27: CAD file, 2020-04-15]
3D-Print/Squeezer V2.FCStd
88.0 x 180.4 x 245.1 mm

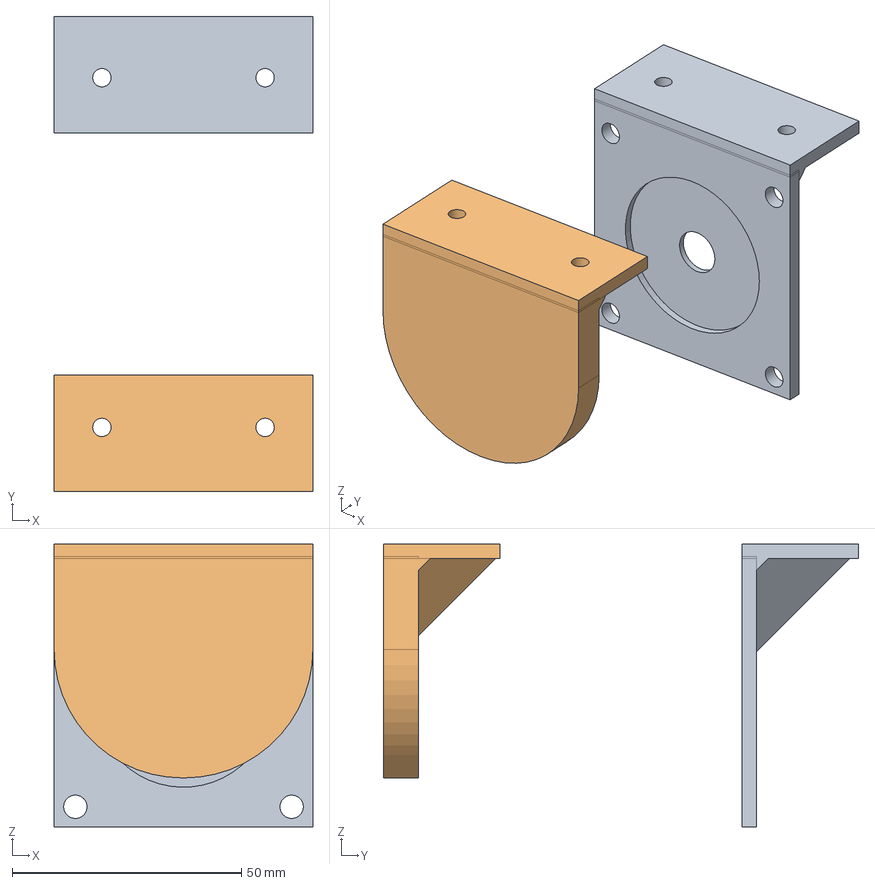
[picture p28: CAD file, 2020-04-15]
3D-Print/NEMA23Flange.FCStd
56.4 x 103.5 x 61.6 mm

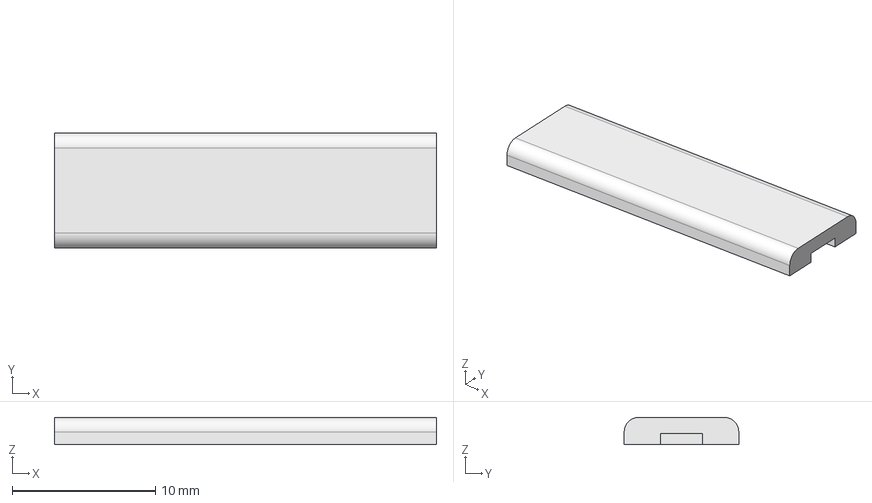
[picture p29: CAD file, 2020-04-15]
3D-Print/Webbing Lock.FCStd
26.7 x 8.00 x 1.91 mm

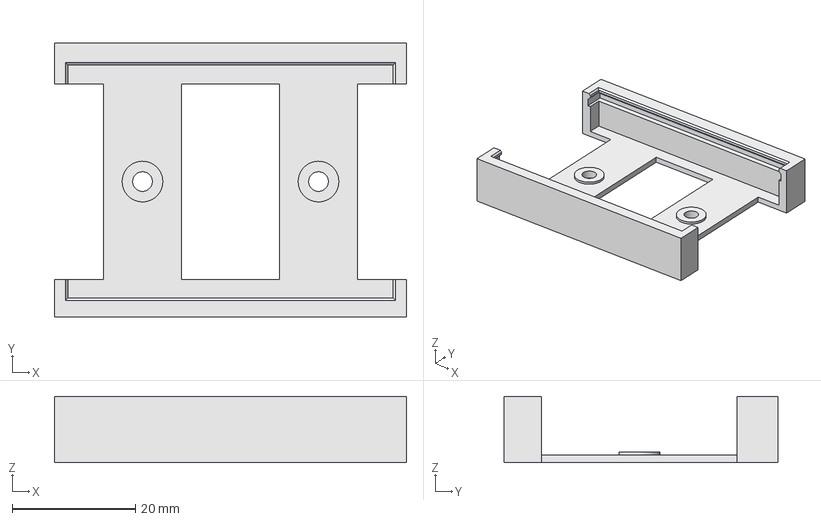
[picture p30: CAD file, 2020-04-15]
3D-Print/Nanoterminal.FCStd
57.1 x 44.5 x 10.8 mm

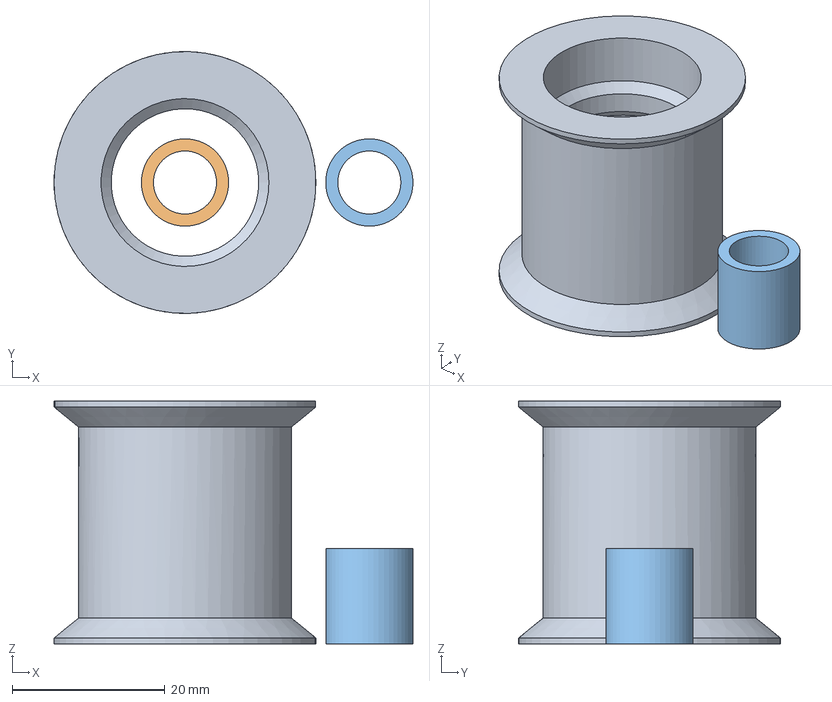
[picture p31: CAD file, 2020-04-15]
3D-Print/roller.FCStd
47.0 x 34.3 x 31.8 mm

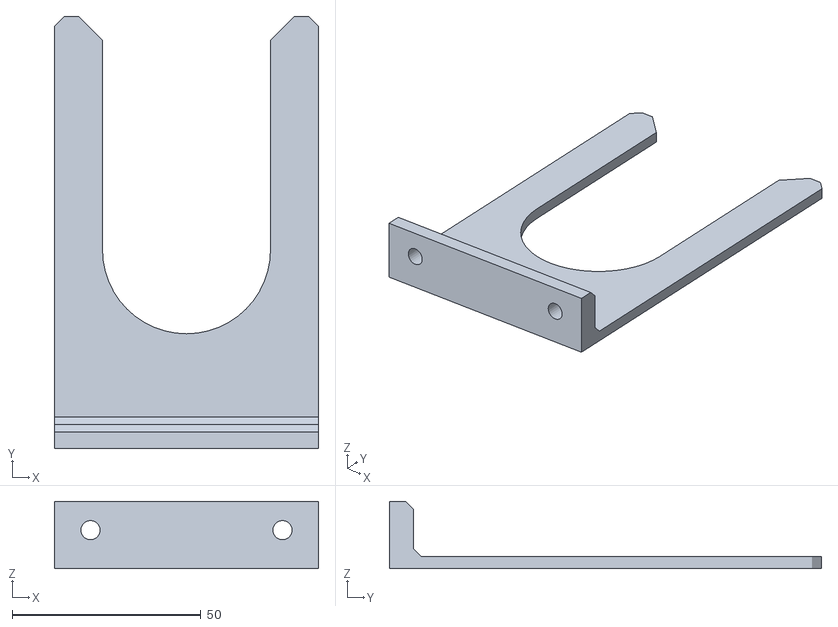
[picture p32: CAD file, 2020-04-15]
3D-Print/Ambu-Bag 2 support.stl
69.8 x 114.3 x 17.8

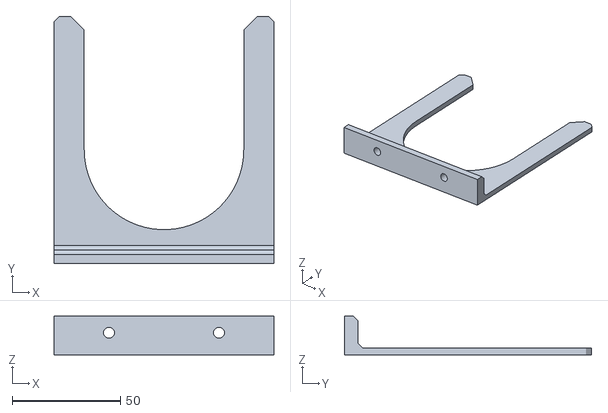
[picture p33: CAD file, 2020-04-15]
3D-Print/Ambu-Bag 1 support.stl
101.6 x 114.3 x 17.8

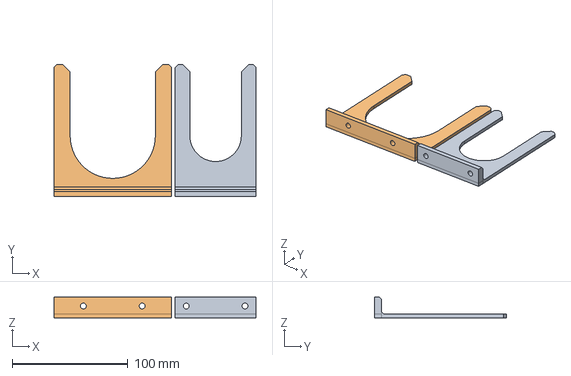
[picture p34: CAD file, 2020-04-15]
3D-Print/Ambu-Bag supports.FCStd
174.6 x 114.3 x 17.8 mm

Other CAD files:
CNC/Box-1.dxf
3D-Print/Panel.FCStd
3D-Print/BearingFlange.stl
3D-Print/NEMA23 Flange.stl
3D-Print/NanoTerminal.stl
3D-Print/Panel.stl
3D-Print/RollerHolder.stl
3D-Print/Squeezer V2.stl
3D-Print/Webbing Lock.stl

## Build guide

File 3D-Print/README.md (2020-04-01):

This is a front panel containing a 2 lines x 16 character module, 5 buttons and a buzzer.

The rear part of the panel holds the display and buzzer in place. Shockproofing requires the 4 2.5mm screws on the display board.

Both the printer ready .stl file and the FreeCAD source drawing are provided.

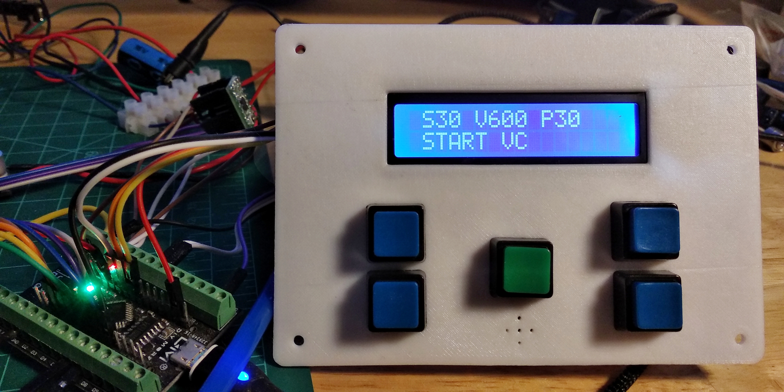
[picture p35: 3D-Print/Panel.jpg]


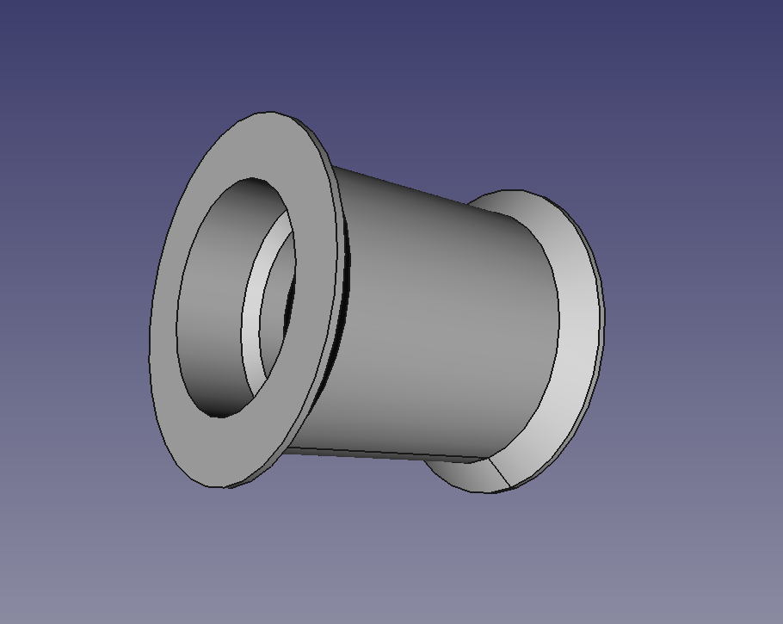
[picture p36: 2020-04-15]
3D-Print/Roller.png

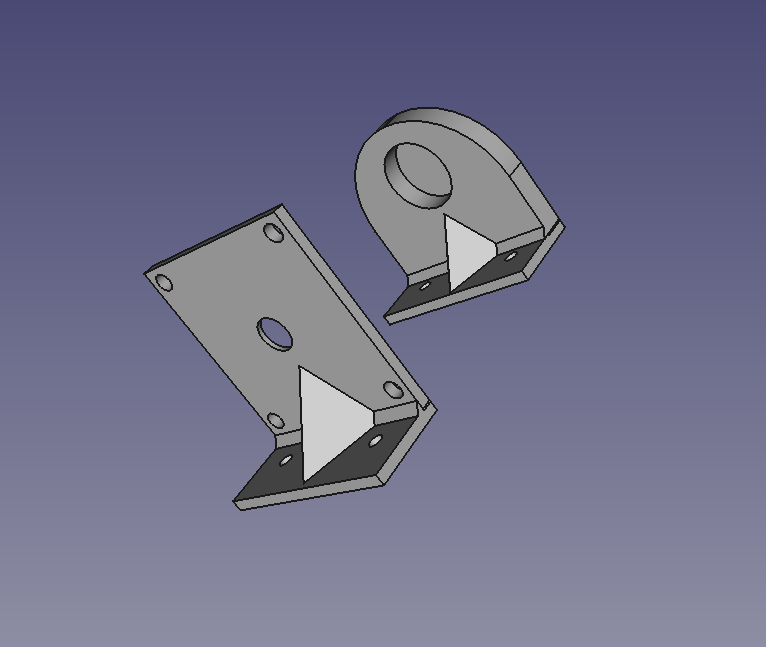
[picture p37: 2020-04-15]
3D-Print/NEMA23 Flange.png

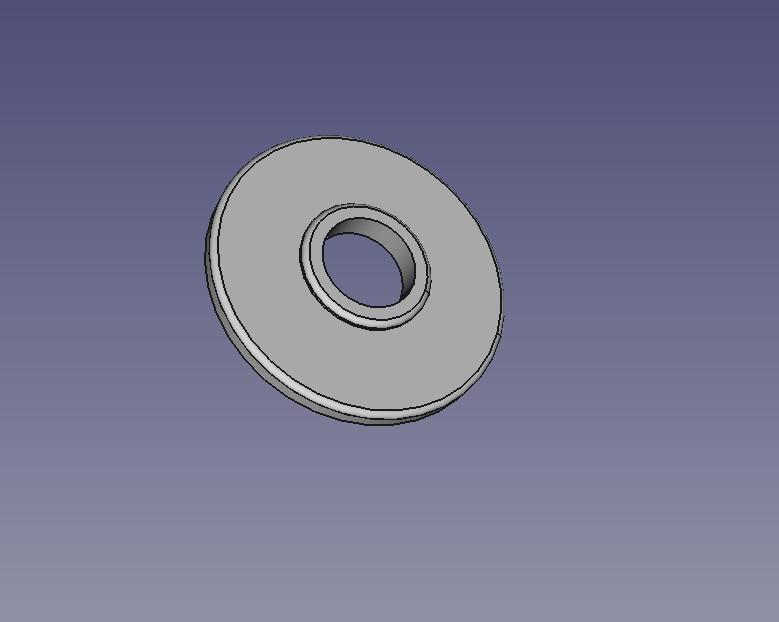
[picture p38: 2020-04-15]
3D-Print/BearingFlange.png

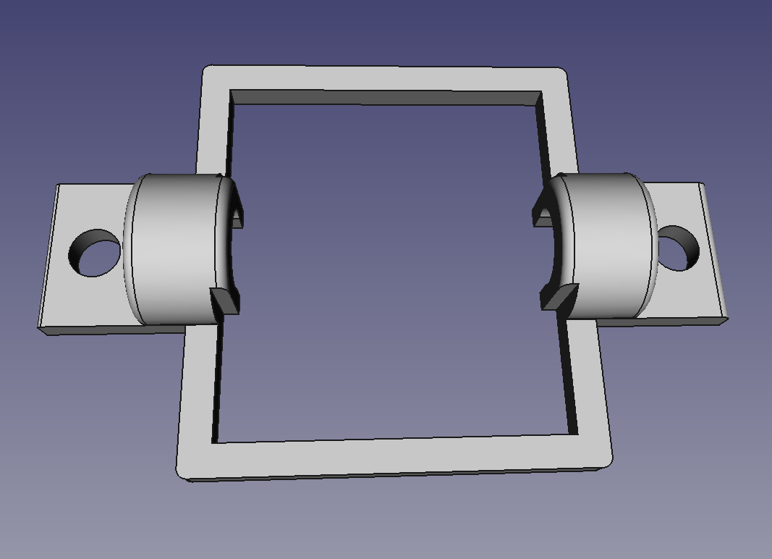
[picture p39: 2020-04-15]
3D-Print/RollerHolder.png

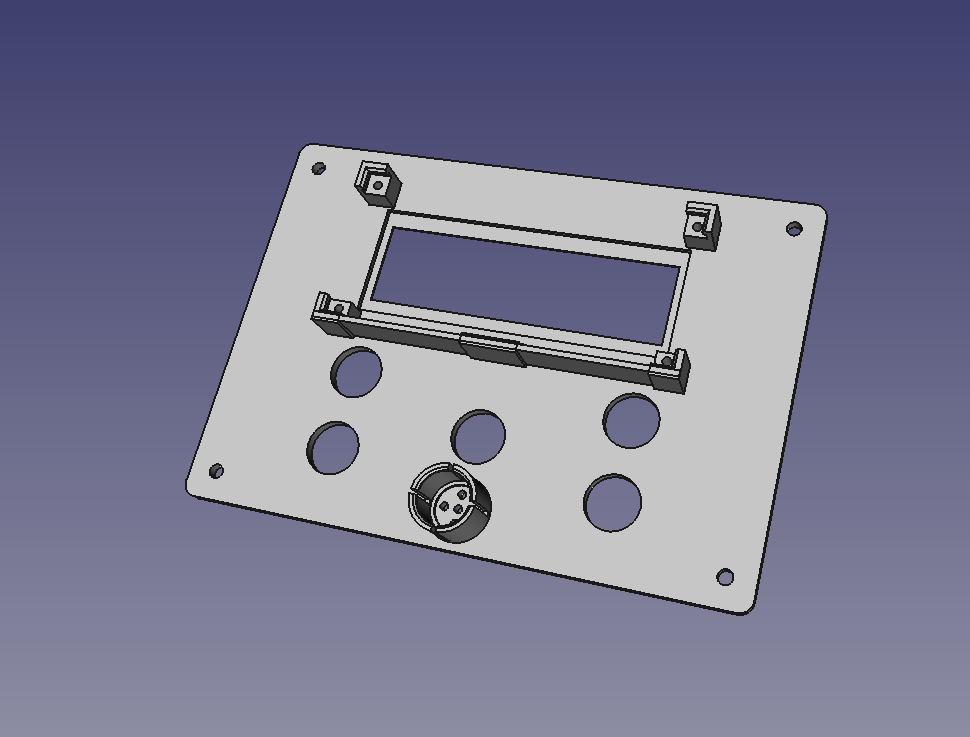
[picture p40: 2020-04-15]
3D-Print/Panel.png

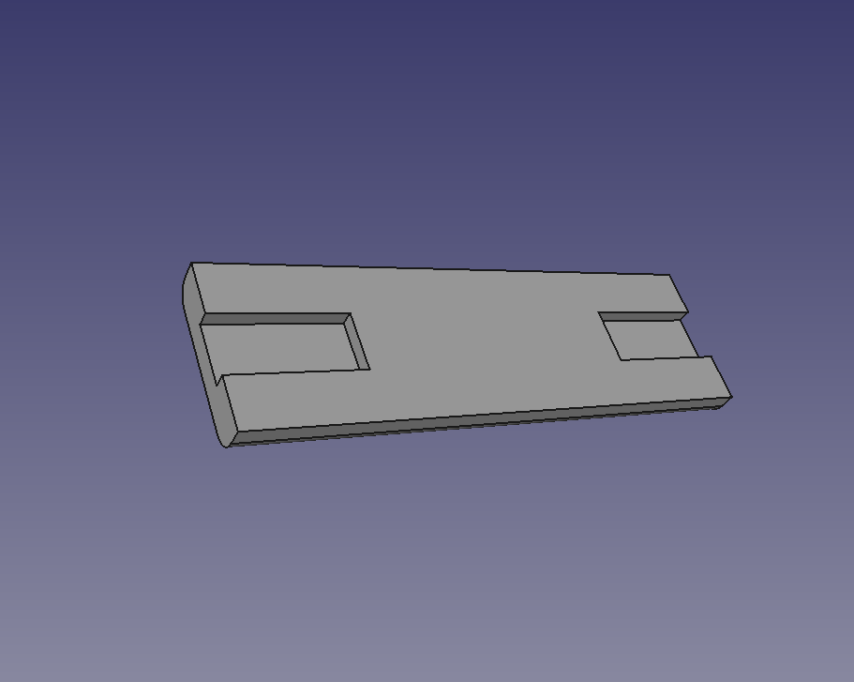
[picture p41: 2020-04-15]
3D-Print/Webbing Lock.png

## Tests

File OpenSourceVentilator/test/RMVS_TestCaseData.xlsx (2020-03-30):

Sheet: VCVT-Compliance
Volume Controlled Ventilation Test (Compliance)
Test No | Test Lung Compliance ml/cmH2O ± 10% | Test Lung Resistance cmH2O/l/s ± 10% | Tidal Volume mls | Rate Min -1 | I:E | O 2 % | PEEP
1 | 50 | 5 | 500 | 20 | 1:2 | 50-60 | 5
2 | 50 | 5 | 500 | 20 | 1:2 | 90-100 | 5
3 | 50 | 5 | 500 | 12 | 1:2 | 50-60 | 5
4 | 50 | 5 | 500 | 12 | 1:2 | 90-100 | 5
5 | 50 | 5 | 500 | 20 | 1:2 | 50-60 | 10
6 | 50 | 5 | 500 | 20 | 1:2 | 90-100 | 10
7 | 50 | 5 | 500 | 12 | 1:2 | 50-60 | 10
8 | 50 | 5 | 500 | 12 | 1:2 | 90-100 | 10
9 | 50 | 5 | 500 | 20 | 1:2 | 50-60 | 15
10 | 50 | 5 | 500 | 20 | 1:2 | 90-100 | 15
11 | 50 | 5 | 500 | 12 | 1:2 | 50-60 | 15
12 | 50 | 5 | 500 | 12 | 1:2 | 90-100 | 15
13 | 20 | 5 | 500 | 20 | 1:2 | 50-60 | 5
14 | 20 | 5 | 500 | 20 | 1:2 | 90-100 | 5
15 | 20 | 5 | 500 | 12 | 1:2 | 50-60 | 5
16 | 20 | 5 | 500 | 12 | 1:2 | 90-100 | 5
17 | 20 | 5 | 500 | 20 | 1:2 | 50-60 | 10
18 | 20 | 5 | 500 | 20 | 1:2 | 90-100 | 10
19 | 20 | 5 | 500 | 12 | 1:2 | 50-60 | 10
20 | 20 | 5 | 500 | 20 | 1:2 | 50-60 | 10
21 | 20 | 5 | 500 | 20 | 1:2 | 50-60 | 15
22 | 20 | 5 | 500 | 20 | 1:2 | 90-100 | 15
23 | 20 | 5 | 500 | 12 | 1:2 | 50-60 | 15
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

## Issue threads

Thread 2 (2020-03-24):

ermtl/Open-Source-Ventilator #2: No schematic available

ZakCodes, 2020-03-24:
As far as I know, there is currently no schematic of your system available on GitHub. Therefore, there's no way for people to understand how to reproduce your circuits.

If you haven't done your design in any CAD software, you can always post a drawing in the comments of this issue and someone could do the schematic in [Fritzing](https://fritzing.org/), [Eagle](https://www.autodesk.com/products/eagle/overview), [KiCad](https://www.kicad-pcb.org/), [LibrePCB](https://librepcb.org/) or whatever.

The important is for people to be able to reproduce your hardware as quickly as possible.

ermtl, 2020-03-24:
You are right, a schematic diagram is in the Todo list and it would be important to have it.
Would you like to do it ? (if possible with Kicad) That would really be helpful.

As of now, the various pins used are listed in the source code, here is the snippet:
```
//********************************   CONNECTION PINS   ********************************

#ifdef TM1638
#define  pin_Strobe_TM         2
#define  pin_Clock_TM          3
#define  pin_DIO_TM            4
#endif

#ifdef I2C
#define pin_SDA               A4
#define pin_SCL               A5
#endif

#ifdef Beeper
#define pin_Beep               8
#endif

#ifdef Led
#define pin_LED               13
#endif

#ifdef stepDirMotor
#define pin_Stepper_DIR        6
#define pin_Stepper_Step       7
#define StepGen
#endif

#ifdef disableMotorctrl
#define pin_Stepper_Disable    5
#endif

#ifdef CurrentSense
#define pin_current_Sense     A3  // do not use A6 or A7 presence detection needs a regular pin with pullup
#endif
```

ZakCodes, 2020-03-24:
Sure! I only have experience with Eagle, but I'll figure out how to use KiCad and I'll do it. I'll try to be done with it today and I'll keep you updated with my advancements at least every day if I don't finish today. However, I live in Québec, so I'm in lockdown right now and I don't have much else to do.

ermtl, 2020-03-24:
Nice !
KiCad 5 is much better than the previous versions, and it seems like a good time to learn it ...

BTW, I'm from Montreal.

ZakCodes, 2020-03-24:
I did see that you were from Montreal from your Youtube Channel name lol. I'm from Montreal too, but I live in Gatineau right now. Are you at home right now or do you work for an essential service? Personnally I'm a student, so I'll be at home until May 1st.

ZakCodes, 2020-03-24:
I have sketched out the schematic of what I think you've done and I think that I have everything right. 
[image]

However, I read the [UK's Rapidly manufactured ventilator system specification](https://www.gov.uk/government/publications/coronavirus-covid-19-ventilator-supply-specification/rapidly-manufactured-ventilator-system-specification#gas-and-electricity) and it is mandatory to have a 20min battery backup and to have an alarm go off whenever power gets disconnected.

I've searched for [`battery backup circuit`](https://www.google.com/search?q=battery+backup+circuit&tbm=isch) on Google and I found circuits looking like this one again and again:
[image]
When the power is connected and the battery is slowing charging and the LED turns on. As soon as it's disconnected, the battery gets used instead and the LED turns off.

This circuit could be slightly modified so whenever the power get's disconnected, an alarm gets turned on. A voltage divider could also be used to read the battery's voltage and therefore level with the Arduino Nano.

ZakCodes, 2020-03-24:
Here's what I mean:
[image]

It might also be possible to find a 12V UPS

ermtl, 2020-03-25:
Your first schematic diagram is incomplete. I see a nano, but not much else.
The power supply is more complicated. To get torque from the motor, you need at least 24V 1A to 2A peak, so the supply needs a step-up converter. Nanos can withstand 12V, but it's not spike resistant, so we need a 2nd regulator for the +5V.
The machine should be able to get power from a regular wall wart 9 or 12V, up to around 22V if people use a laptop supply (all without releasing the magic smoke). 
For the battery, I'm currently looking at designing a 3D printed socket for Bosch cordless drill batteries as they are ubiquitous, powerful and have their own charger.
Maybe we should discuss this in the slack at https://osventilator.slack.com 

If you do a schematic diagram, the first thing would be to start from the modules and show how to interconnect them. Maybe it's more of a Fritzing thing, after all...

ZakCodes, 2020-03-25:
Fritzing would indeed probably be a better idea.

I tried to sketch the schematic while only knowing about the 7 parts listed in the README file of this project, so I didn't even realize that the motors were powered with 24V and that they had a charge pump circuit to make 24V out of 12V.

Now I've taken a closer look at the Youtube video you posted and saw the capacitor for what I believe is the charge pump circuit, however I'm not sure.

Except for the charge pump circuit, is there anything else I need to change?

uxvrob, 2020-03-26:
Hey @ZakCodes I've been working on adding this circuit to the OpenLung project.  
Rev2 has some errors but should be fixed by tomorrow.
The design most likely will diverge from Erics' so haven't add the beepers and TM1638. 
Would you like me to make an exact copy of the circuit like Eric's?
https://gitlab.com/uxvrob/OpenLung/-/tree/feature/issue109/concepts/controller-concept-1/P1A1/kicad/sch_pdf

ZakCodes, 2020-03-26:
You could do. I tried making the schematic for this project, but I genuinely don't understand how the motor are powered since Eric said they are powered with 24V and they need a charge pump circuit, but I don't have any details on whether he made a custom charge pump circuit or whether he's using an existing part.

I'm stuck right now, so if anyone knows how to do it, please do it, because I don't want to slow down anything.

uxvrob, 2020-03-26:
Would a fritzing version be helpful? I can do the kicad schematic then perhaps you could help draw up a fritzing version for better visuals.

ermtl, 2020-03-26:
ZakCodes:
I actually use a 24V supply, but in a final version, we want it to also be compatible with 12V sources that are far more common, such as wall warts, 12V batteries, 20V drill batteries, 16V to 24V laptop supplies, etc ...

Thanks to [uxvrob](https://github.com/uxvrob) we now have a [complete schematic diagram](https://github.com/ermtl/Open-Source-Ventilator/blob/master/hardware/OpenSourceVentilator_Rev1.pdf) so that the controller can be tested.

Should we make a Fritzing version, or consider the issue closed ?

ermtl, 2020-03-27:
uxvrob Is now doing the schematic diagrams for the project, thanks to everyone !

closed 2020-03-27 by ermtl

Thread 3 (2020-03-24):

ermtl/Open-Source-Ventilator #3: Configure the CI with GitHub Actions

ZakCodes, 2020-03-24:
It would be cool to have the CI configured for this project. I've configured the CI for an Arduino project on GitLab before by using [arduino-cli], which you can see [here](https://gitlab.com/chapeau-melon/controleur-serre/-/blob/master/.gitlab-ci.yml) (the project is french, sorry).

In the project I just linked, the CI includes the following thing:
* [ ] Compiling the project using [arduino-cli]
* [ ] Checking the code formatting against a code convention using [clang-format]
* [ ] Generating HTML documentation from the source code using [Doxygen] and publishing it to GitLab Pages (it could be published to GitHub Pages for this project)

It would also be cool to add a badge with the CI status in the README file like so many projects do like so:
```md
![Build Status](https://github.com/actions/hello-world/workflows/Greet%20Everyone/badge.svg)
<!-- 
This was taken from: 
https://help.github.com/en/actions/configuring-and-managing-workflows/configuring-a-workflow#adding-a-workflow-status-badge-to-your-repository 
-->
```

To do all this on GitHub, [GitHub Actions] is probably the best thing to use right now, since it is directly integrated into GitHub. However, there are other services available like [TravisCI](https://travis-ci.org/), [CircleCI](https://circleci.com/) and [Jenkins](https://jenkins.io/), but they require more configuration than [GitHub Actions].

To help with setting up the different stages of the workflow, the following [GitHub Actions] helpers would be good to use:
* [setup-arduino-cli](https://github.com/arduino/setup-arduino-cli): made by Arduino, configures [arduino-cli] to run in workflows
* [clang-format-action](https://github.com/cvra/clang-format-action): use clang-format to format C/C++ files using a coding standard
* [doxygen-action](https://github.com/mattnotmitt/doxygen-action): generate html docs using [Doxygen]

[GitHub Actions]: https://help.github.com/en/actions
[arduino-cli]: https://github.com/arduino/arduino-cli
[clang-format]: https://clang.llvm.org/docs/ClangFormat.html
[Doxygen]: http://www.doxygen.nl/

mattd3v, 2020-03-24:
I will look at doing this very soon!

mattd3v, 2020-04-09:
PR #31 sets up and compiles the project.

karx, 2020-04-17:
https://gitlab.com/open-source-ventilator/ventilator/OpenLung/-/issues/146 is a parallel issue to this over on GitLab.

karx, 2020-04-17:
To tackle the issue of `jm_wire` I created forks for the 2 libraries that needed to be updated.

* [BM280](https://github.com/karx/BME280)
* [LiquidCrystal_PCF8574](https://github.com/karx/LiquidCrystal_PCF8574)

And used git to clone these libraries instead of Arduino library manager. The [build](https://gitlab.com/kaaro/controller_ci_demo/pipelines/137341800) is passing now using this.

ladvine, 2020-04-26:
@karx When i use the original jm_Wire library, i am too facing issues.
I will make the CI build to use the libraries maintained in GitHub.

karx, 2020-04-27:
@ladvine awesome! 

So these builds will run on all PRs and add label?

ladvine, 2020-04-28:
> @ladvine awesome!
> 
> So these builds will run on all PRs and add label?

It will run on all PRs. But following things are still pending:-
1. Add label when build is successful.
2. Checking the code formatting against a code convention using clang-format
3. Generating HTML documentation from the source code using Doxygen and publishing it to GitLab Pages (it could be published to GitHub Pages for this project)

nimamoslemy, 2020-05-01:
Hi, we are a team that needs your feedback to complete our idea.
Please visit our pages and comment on it. 
[github](https://github.com/nimamoslemy/ventilator)
[gitlab](https://gitlab.com/nimamoslemy/avp-ventilator)

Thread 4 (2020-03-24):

### ISSUE TITLE
Document how to configure and upload the code to an Arduino

### ISSUE THREAD

**Issue by ZakCodes** [ermtl/Open-Source-Ventilator#4]
It would be nice to specify in the README.md or in the CONTRIBUTING.md what libraries to install (and maybe their versions) for this project to compile as well as how to compile and upload this project.

There could be links to the following official Arduino guides:
* How to install the Arduino IDE
  * [Windows](https://www.arduino.cc/en/guide/windows)
  * [Linux](https://www.arduino.cc/en/guide/linux)
  * [MacOS X](https://www.arduino.cc/en/Guide/MacOSX)
* [How to use the Arduino IDE](https://www.arduino.cc/en/Guide/Environment#toc9), among other things, this explains how to upload to a board
* [How to install libraries](https://www.arduino.cc/en/guide/libraries)

There should also be more explanations on how to disable certain sensors in the code. It's really a great feature and people really need to know how to use it.

<br>

I would also like to point out that the [Arduino IDE] is awful and that using [VS Code] with the [Arduino extension][Arduino VS Code] should be considered, since it offers autocompletion. However, from my experience with the ESP32 and ESP8266, compile times are longer when using it.

Another option would be to use [PlatformIO] with the [Arduino Framework](https://docs.platformio.org/en/latest/frameworks/arduino.html) on [VS Code]. This is my favorite one, because [PlatformIO] has a configuration file which would allow people who want to compile and upload this project to a board to enter a single command in the terminal or to click a single button in [VS Code] to [download all the required Arduino libraries with the right version for the project](https://docs.platformio.org/en/latest/projectconf/section_env_library.html#lib-deps). Their extension also offers better autocompletion than the [Arduino extension for VS Code][Arduino VS Code]. However, [PlatformIO] has a very specific folder structure for code which I believe is great, but would require this repository to be reorganized a little and it wouldn't be compatible with the [Arduino IDE] or the [Arduino extension for VS Code][Arduino VS Code] anymore.

[Arduino IDE]: https://www.arduino.cc/en/Main/Software
[VS Code]: https://code.visualstudio.com/
[PlatformIO]: https://platformio.org/
[Arduino VS Code]: https://marketplace.visualstudio.com/items?itemName=vsciot-vscode.vscode-arduino

**Comment by ermtl** [comment]
Arduino, for better or worst, is what a majority of people use and that's it's greatest strength. Going to any other platform would severely limit audience and, as you mention, would cause issues with the regular Arduino platform. Also, it's all happening in a rushed situation, I would like to keep it simple.

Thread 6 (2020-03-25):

ermtl/Open-Source-Ventilator #6: Program / EEPROM memory integrity check library

ermtl, 2020-03-25:
Sometimes, mostly after a few years (or less in case of hardware defect), processor program memory or it's EEPROM start to lose their content, sometimes in elusive / voltage and/or temperature dependant ways. When that happens, the program will behave erratically, hang, and fail to execute it's intended function. Same can happen if the EEPROM is corrupted. 

In a project where the machine's proper functioning is critical, this can't be allowed to happen.

Newer AVR processors (and others) offer hardware program / EEPROM memory integrity check.

A complete description can be found in the [ATMEGA4809 datasheet](http://ww1.microchip.com/downloads/en/DeviceDoc/ATmega4808-4809-Data-Sheet-DS40002173A.pdf) starting at page 370.

For processors that don't have it, the function can be made using software.
The basic function is to scan the whole program memory and calculate a CRC. The computed CRC is compared to several copies of the previously calculated value stored in multiple locations on the EEPROM. If it fails, the program acts accordingly (generally it should just  write an error code to EEPROM and stop. Upon the next start, an error message should be displayed to alert the user that the machine could be unreliable.
Same can be done with EEPROM (must be separated as the operation should be done after each EEPROM update).

I could not find a library that implement this. Would anyone be interested in programming one (as a separate, independent project) ?

ZakCodes, 2020-03-25:
EEPROM corruption is probably the most likely failure to happen, since the MCU could shut down while writing to the EEPROM and corrupt it.

However, here's what is said in the [ATMEGA328P's datatsheet](http://ww1.microchip.com/downloads/en/DeviceDoc/Atmel-7810-Automotive-Microcontrollers-ATmega328P_Datasheet.pdf#G1176791) about data retention:
> Reliability qualification results show that the projected data retention failure rate is much less than 1 PPM over 20 years at 85°C or 100 years at 25°C.

Since this project is more for emergency and that the MCU shouldn't get used for 20 years, we can expect even less than 1PPM to fail. It would have been nice from Atmel/Microchip to give us a graph of the number of PPM to fail based on their age and the temperature.

Blimpyway, 2020-03-25:
I recall talks on arduino forum where people tested arduino's eeprom failing at up to 1M write cycles. The specs is 100k cycles.  So.. I wouldn't worry too much. If power fails there is a more immediate problem than what happens when the arduino reboots.

Blimpyway, 2020-03-25:
A blank eeprom is all 0xFF I think. Power failure exactly in that sub- millisecond which arduino needs to update a value is very unlikely.

ermtl, 2020-03-25:
Most Arduino projects are controlling gizmos that blink.
This one is about people's lives. a bug that results is over pressure in the lung can kill the patient or damage their lungs and make them short breathing for life.
If you were the patient, would you take "I wouldn't worry too much" for an answer ?
That's why automotive and medical designs require these kind of checks.

ZakCodes, 2020-03-25:
@Blimpyway I agree. It is really unlikely, especially considering that data is only written to the EEPROM whenever a user is changing its configuration. However, it shouldn't be too hard to compute a CRC of the EEPROM every time we write to it, so I think it's worth it if it can prevent an accident.

Blimpyway, 2020-03-25:
Ok. Simple xor-ing 255x32bits int (or even adding) chunks  and writing the result on the 256-th should be more than enough. On reboot xor-again, if the sum does not match just beep an alarm and do nothing. Whoever operates it will have to dial in all settings.  If that is ok for you I'll write it

ermtl, 2020-03-25:
There are reasons why CRCs exist, and that's because they are much more resistant than basic XOR. When memory corruption errors occur, that's often in clusters. If 2 bytes are affected, a CRC check won't see it. That's why CRC16 or CRC32 is needed and the check has to be done on the program memory as well as the EEPROM. 

The mindset when developing safety critical devices is very different from the maker mindset where the job is considered done as soon as the main function kind of works. Here, we must be sure that it will always work as intended.

https://en.wikipedia.org/wiki/Cyclic_redundancy_check
https://en.wikipedia.org/wiki/Hamming_distance

Blimpyway, 2020-03-25:
[failtest.zip](https://github.com/ermtl/Open-Source-Ventilator/files/4381841/failtest.zip)

Here-s a zip file with 
- ee_failsafe.ino which can be added as a tab to your project. 
- failsafe.ino - just to show how the two functions eeprom_write_crc() and eeprom_test_crc() should be used. 

And yes it's using a slightly modified CRC32 sum I picked from arduino.cc examples.  The change just skips the EEPROM memory slot where the crc itself needs to be saved. This address can be redefined in ee_failsafe.ino
e.g. 
#define SKIP_ADDRESS  16

Blimpyway, 2020-03-25:
feel free to ask me if anything isn't clear.

Blimpyway, 2020-03-25:
If we-re to share thoughts about critical systems guidelines, then people lifes should not depend on  software/mechanics developed in <4 weeks no matter how good designers are.

ermtl, 2020-03-25:
That was fast !
I'll test it tonight. Can you also add the ability to scan the program memory ?
The test should be done only until the end of the program, else, previously written programs will appear as random garbage and the value will not be the same from one device to the next.

I agree with you about the short time, unfortunately we don't get to decide about that, that's why it's an emergency. Normally such stuff takes months if not years for a whole team to develop.

Blimpyway, 2020-03-27:
If you really want it to be safe, take it functionally. I mean have a function that checks correct pressure swings are registered and reset the wdt in the same place.  Medics already want to be alerted if pressure gets too low or too high. Add an alert for pressure not changing. This covers pressure sensor / I2C failure, air leakage, bag exploded stepper unplugged and whatever other part of code not going right. If pressure swings are recorded at the mouth of the patient then chances are s/he is not dead yet.  If sensor contamination is acceptable (it might be autoclavable since it is made to resist soldering) it can even sense exhalation temperature or, at least it can tell the patient isn't entirely cool.

mawaisbadri, 2020-03-28:
One solution to resolve eeprom write problem is soft shutdown circuit, So MCU can shutdown whole system. 2nd precaution is to save eeprom values on multiple locations at same times. means one value is being saved in three EEPROM locations at same time. On reading, read three locations and check if three are same?
3rd one is add separate safe guard circuits for critical things.
Hope it helps.

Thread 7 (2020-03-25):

ermtl/Open-Source-Ventilator #7: Canary memory / stack check.

ermtl, 2020-03-25:
To detect memory & stack corruption, a known good and easy way is to add canaries. 
For good protection, all the canaries should not have the same value and they should be spread among other variables and several of them (8seems reasonable) should be put, if possible at both ends of the stack and at both ends of the variables area.
Any corruption detected by the checking function means something seriously wrong happened. If it happens, it should just write an error code to EEPROM and call a handler. Upon the next start, an error message should be displayed to alert the user that the machine could be unreliable.

the handler should decide what to do next. Usually activate an alarm and maybe stop. For a medical device, we should ask advice from a MD about the best option (stop or keep going with a serious risk).

An important point is to look at the resulting assembly code and check that the compiler did not "optimize" the canaries either by removing them, merging them or grouping them all together. also the stack canaries location relative to the variables and stack should be checked.
This is a job for a compiler wizard ! 

Info about canaries:
https://en.wikipedia.org/wiki/Buffer_overflow_protection#Canaries
Info about stack overflows and stack canaries:
https://en.wikipedia.org/wiki/Stack_buffer_overflow

This not being specific to the project, it could be done as a as a separate, independent project.

mattd3v, 2020-03-25:
Could the use of more C++ STL data structures help manage overflows, without adding as much code?

Blimpyway, 2020-03-26:
I worry more by not having a [watchdog timer](https://en.wikipedia.org/wiki/Watchdog_timer).
  
What do you mean by code corruption? AVRDUDE (or other flasher) does verify the code after it was written. Do you really think you (or something else like the program itself or an EMP) can change after it was flashed ?  
If this was a thing somebody on either arduino  or avrfreaks forum would  freak about it. 

[wdt_example.zip](https://github.com/ermtl/Open-Source-Ventilator/files/4386675/wdt_example.zip)

ermtl, 2020-03-26:
mattd3v: Do you have an example of those structures being used on an Arduino ?

Blimpyway : The final code will have a watchdog timer. I did not add it for now as if people make mistakes in the code, it's easy to brick the board, and the program will need to be wiped out completely, reflashing the bootloader won't help. So people trying the code would lose their hardware (not everyone knows how to flash the entire chip).

If you look in my other repository, I worked on a version of the Adafruit_Sleepydog and added a mod that prevent bricking Chinese clones. I'll have to make it into a different library as Adafruit did not accept the pull.
https://github.com/ermtl/Adafruit_SleepyDog

miguel5612, 2020-03-30:
#ifdef Canary
disable sensorFeature and safe memory
#endif
Same to arduino pro mini ATMEGA 168

ahogen, 2020-04-05:
That watchdog example looks cool!

The GCC compiler flag [`-fstack-protector`](https://gcc.gnu.org/onlinedocs/gcc/Instrumentation-Options.html#index-fstack-protector) will [call ](https://antoinealb.net/programming/2016/06/01/stack-smashing-protector-on-microcontrollers.html)a `void __stack_chk_fail(void)` function if stack corruption is detected. Also the flag [`-fstack-limit-symbol=__StackLimit`](https://gcc.gnu.org/onlinedocs/gcc/Instrumentation-Options.html#index-fstack-limit-register) is interesting (where [`__StackLimit` is a symbol](https://www.silabs.com/community/mcu/32-bit/knowledge-base.entry.html/2018/11/11/understand_the_gnua-zyam) from the linker script). Those options require modifying compiler flags, which isn't simple or convenient to do in the Arduino IDE.

The project could use a [Makefile](https://github.com/sudar/Arduino-Makefile) where the build arguments can be controlled by this project instead of the Arduino Foundation.

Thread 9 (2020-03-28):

ermtl/Open-Source-Ventilator #9: A few more resources

Blimpyway, 2020-03-28:
Hi I'll add here links and docs I find useful, you decide whether you want them included in the project. 
A couple good tutorials about how to configure A4988 and DRV8825 stepper motor drivers: Most tricky one is current limit adjustment which is slightly different for the two drivers. 
- A4988:  https://www.makerguides.com/a4988-stepper-motor-driver-arduino-tutorial/
- DRV8825: https://www.makerguides.com/drv8825-stepper-motor-driver-arduino-tutorial/

Attached is a drv8825.pdf, which can replace A4988. You already have A4988 pdf 
[drv8825.pdf](https://github.com/ermtl/Open-Source-Ventilator/files/4397039/drv8825.pdf)
 
Program /circuitry should not be affected they can replace each other in 3d printer boards.

ermtl, 2020-03-30:
Thanks, there are several motor drivers that can be used with it. Drv8825 is interesting as it has higher voltage ability, however, latest calculations show we'll probably need a beefier motor and associated driver.

Something like this one:
https://www.aliexpress.com/item/32714985325.html

closed 2020-03-30 by ermtl

Blimpyway, 2020-04-01:
According to my [testsl](https://drive.google.com/drive/folders/1WHIIuMprFZx8wzUte5k5reL2CMoxuLD7?usp=sharing), a Nema17 with DRV8825 (and likely A4988 since it is tuned at under 1.2A) is fully capable to deliver pressure/volume/bpm needed.

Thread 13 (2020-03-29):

ermtl/Open-Source-Ventilator #13: BME280 pressure 3d printed part

miguel5612, 2020-03-29:
Hi, we are trying to reply your respirator, but how to install bmp 180 into a tube?

ermtl, 2020-03-30:
It's a BMP280. As of now, the library implements BMP180 only for the secondary ambiant pressure sensor.
The BMP280 module is inside a syringe as you can see in the picture. The real one would be similar, but using a round cable passing in the middle of the elastic part of the syringe plunger so that it's in front of it, and the plunger makes it airtight. It's very important, else, humidity will always be 100% and wet electronics don't work too well for too long ...
The syringe I used contains a LUER connector and tube adapter. That's a standard connector for medical devices.
Most ambu-bags have a sensor outlet where you connect the tube. The sensor will stay in the machine, the tube is not a problem for the measurement as long as it's not kinked, same as commercial machines. We don't bring the sensor close to the patient to prevent exposure to electrical devices (that would require a special medical grade, expensive double insulation power supply) and it's also to prevent having long wires as I2C circuits can have all kind of troubles when connected over a distance.

[image]

closed 2020-03-30 by ermtl

miguel5612, 2020-03-30:
Excellent, Thanks :)

Blimpyway, 2020-04-01:
I wish it would use either BMP280 or BMP180 for both respiratory pressure and ambient one.  I mean in many places stocks of BMP280 might run out first and in other places BMP180 I'd hope to be able to go on with either one not being forced to use both. Not assuming in a global crisis global deliveries  work flawlessly so I got any part I order on digikey here tomorrow.

miguel5612, 2020-04-01:
Than you @Blimpyway 
Here is the code modified to allow BMP 180 👯‍♂ 
https://github.com/miguel5612/Arduino_Respirator/blob/master/OpenSourceVentilator/OpenSourceV
entilator.ino

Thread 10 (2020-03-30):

### ISSUE TITLE
Wire.h workaround?

### ISSUE THREAD

**Issue by Blimpyway** [ermtl/Open-Source-Ventilator#10]
Is there any problem with overwriting Wire.h file with the fixed jm_Wire.h? 

I mean besides the fact an eventual arduino IDE upgrade will replace back the wrong one?

**Comment by ermtl** [comment]
Yes, that is another solution, however I did not want to tell people to start patching Arduino's libraries.
As of now, the jm_Wire solution seems the easiest.

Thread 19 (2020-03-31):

ermtl/Open-Source-Ventilator #19: Please use cmH2O for units instead of pascals

gr5, 2020-03-31:
Good work so far by the way!

Pascals is metric and a wonderful unit.  However everyone is talking cmH2O.  Doctors, hardware designers, literature, other ventilators, everyone.  And I can trivially measure pressure by sticking a hose down into so many cm of water and making bubbles.

I know it's trivial to convert from one to the other but when you are debugging (like if you hit the P command for example) you want both internal variables and also displays to show everything in the same units.  There is less confusion, fewer bugs introduced, and debugging is slightly faster.

The exception might be the ambient (not ambiant by the way - it's misspelled somewhere) pressure.  This could be in any unit you prefer as it's the only thing we care about that is *absolute* pressure.  In this case pascals is fine, or mm of mercury or whatever.  Everything else will be relative pressure (relative to ambient or relative to each other).

Blimpyway, 2020-04-01:
Sensor libraries report absolute pressure in pascals. 

Medical equipment literature also refers to hPa (hecto-pascals = hundreds of pascals) which is equal to cmH20 . There are 1000 hPa and 1000cm H20 in an atmosphere.  

Anyway reporting a value within 1000 +/-50 cm range could also be confusing to someone expecting a few dozen cm.

ermtl, 2020-04-01:
I fully agree. I started with the sensor's native unit, but in the medical world, everyone uses cm H2O, the unit for pressure will be changed in the next version.
For 'ambiAnt' that's what happens when I mix up French and English ! Corrected, thanks.
atmospheric pressure will probably stay in Pa. Anyways, it's measured just to be subtracted from the actual measurement in cases where there is no relative pressure sensor (I'm waiting for some)

gr5, 2020-04-01:
You can probably abbreviate to "cm" if you want the unit in the variable name.  Although I see you don't seem to have that habit (which I like but I'm happy either way - sometimes known as hungarian notation or a variant - named after a hungarian software architect at microsoft).

@Blimpyway - hPa is okay but I prefer cmH2O even though they are only 2% different.  For absolute pressure, I agree Pa is a good choice for unit.

ermtl, 2020-04-02:
@gr5 The pressure unit have been changed as requested, see new V0.21. Closing the issue for now.

closed 2020-04-02 by ermtl

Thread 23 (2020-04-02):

ermtl/Open-Source-Ventilator #23: Break up the source into smaller module realted files

mleyden, 2020-04-02:
Source is now ~2300 LOC in a single file. I would recommend breaking it down. A suggestion would be something like this:
-Open-Source-Ventilator.ino (main)
-config.h (defines)
-ui.cpp (implement a Class-based interface that allows other types of display/keyboard to be used)
  -keyboard.cpp
  -display.cpp
-control.cpp
-sense.cpp
  -pressure.cpp
  -volume.cpp

mawais15, 2020-04-02:
Hi, 
we are trying to use this code in development of an open source ventilator with some modification but it is really hard to go through all the code in one file. It would be really nice if it could be broken down into multiple files.

Blimpyway, 2020-04-02:
I would even go as far as leaving only serial  interaction.  Have a clear, well defined .. "protocol" between a control unit and an interface unit. 

The benefits are several 
- The controlling code becomes simpler, clearer with fewer dependencies 
- More important it can be tested thoroughly independent of UI parts availability and then closed. 
- hardware/mechanical developers can tune specific parameters for their implementation number of steps, type of sensors, etc. without worrying about interface. 
- Whoever develops UI-s can pick either a second uC with buttons/lcd talking serial with controlling unit , or  phone/laptop based on serial over USB/bluetooth/IP channels can easily test/validate their interface without having to touch the actual controlling code. Or even an android/iphone developer can work at an application without having an actual phisical device to script a test protocol.

mleyden, 2020-04-02:
My thoughts on the overall system design. System needs to be tolerant to single faults. See: https://whimsical.com/JBKt1qDAetj2P8nt7EF9nY

mattd3v, 2020-04-09:
I have opened PR #30 and begun working on breaking up the source into smaller modules. Would it make sense to put the EEPROM related code into its own Memory module for device independence, or is that unnecessary?

karx, 2020-04-12:
@mattd3v I think moving them into a module should help. We can maintain the defaults, error correction, and integrity checking there itself. 
#6 

This would also help in having a single point of persistence state kindof a picture. Should help in keeping the code clean.

The module would have to be top-level type. A shared static class maybe, as I am sure many of the other modules we have in the making would be using.

karx, 2020-04-12:
Also, going through the code, I see alot of it is governed by compile-time logic, which seems smart and optimized.

But kindof also gets me rolling in the direction of modularizing in that direction then. Example would be the use of Serial.

It is governed by a few statics: `serialTelemetry`, `serialVerbose`, 'ArduinoPlotter', debug level, and a variable called `term`.

Which makes it quite hard to understand what is happening imo. Let me know what you think.

mattd3v, 2020-04-12:
@karx I share many of the same opinions. Especially, regarding the ambiguity created by the compile time directives. I would also like to extrapolate the debugging code from the core logic.

I’d be interested in splitting the task up? Should we create issues for specific tasks?

karx, 2020-04-12:
> I would also like to extrapolate the debugging code from the core logic.

I would like to know your ideas regarding how to do this.

Sure, if you think you can chunk out a task for me I would like to contribute here.

Although, I must confess here.
I am yet to build this project on my local system. Don't have my usual machine, using my brother's laptop actually. I luckily do have the boards in question, avr-boards and a bunch of ESP32s. 

But pretty sure would not also have the necessary peripherals to test at my end.

karx, 2020-04-12:
In the meantime in order to wrap my head around the codebase, I started to compile these compile-time directives and dynamic variables (haven't reached them yet) into a more readable and sharable format. 

https://github.com/karx/Open-Source-Ventilator/tree/kaaro/refactor/configuration

Have a look and let me know if you have any better ideas on how we can make this more readable.

I have in that document also kind of *proposed* we have a few `admin-type` settings. These would include those settings/variables that can be updated after deployment, to hotfix/error correct/calibrate/hack the device after deployment on-ground.

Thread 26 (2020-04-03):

ermtl/Open-Source-Ventilator #26: No.sensor error 0

Bootpanic, 2020-04-03:
Getting intermittent "NO.SENSOR Error 0"

Stopping and starting seems to trigger error.

I have TM1638 for keys, display and bar graph.
BME280 sensor connected.

Bootpanic, 2020-04-03:
I'm using a Arduino Mega. Don't know if this could be related.

Bootpanic, 2020-04-04:
I have tried with an Arduino Uno. The problem remains the same.

ermtl, 2020-04-04:
First thing, there are 2 kinds of breakout boards for BME280. Some with 3.3V regulators that are designed for 3.3 to 5V, others without, only for 3.3V.
If you have the 3.3V version, connect it's supply to 3.3V, and the I2C pins will be ok (at least for a prototype) since they are open drain.
Then, you can activate #define ArduinoPlotter and within Arduino go to "Tools" / "Serial plotter", you should see the pressure trace (above the motor/cycle traces). If something goes wrong, you should see abnormal values. If the problem shows there, please share a screen capture.

You can also check the sensor with the examples included in the BME280 library.

Also make sure you use the jm_Wire.h library as explained here:
https://github.com/ermtl/Open-Source-Ventilator/blob/master/OpenSourceVentilator/README.md

Bootpanic, 2020-04-04:
First of all thanks for all the great work!

I'm using the Pimoroni BME280 breakout board whis is rated for a supply voltage from 2V to 6V.
The BME280 breakout board is connected the the Arduino 3.3V out.
[image]
https://shop.pimoroni.com/products/bme280-breakout.
Wire length is less than 15cm.
I have turned "#define debug_3      // print sensor datadata" on in the source and the sensordata in serial monitor looks OK when the "No.sensor error 0" is displayed.
I will try to connect the BME280 breakout board to the 5V supply to see if it makes any difference but i doubt it. I will report here as soon as i've tried.
Greetings,
Bootpanic

Bootpanic, 2020-04-04:
I just tried to connect the Pimoroni BME280 breakout to the Arduino 5V supply rail with no change. The error still occurs.  A friend of mine is having the same intermittent error. The error seems to be triggered when stopping/starting the ventilation.

ermtl, 2020-04-04:
This was not a sensor issue, but a mistake in the menu system. I made changes on the 2 lines 16 characters LCD display and and did not test them with the TM1638.
This is corrected in the new V0.23 version. I'll close the  issue for now, feel free to reopen  if needed

closed 2020-04-04 by ermtl

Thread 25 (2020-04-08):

### ISSUE TITLE
Compiling on ESP32 fails: 'byte alarm' redeclared as different kind of symbol

### ISSUE THREAD

**Issue by frippe75** [ermtl/Open-Source-Ventilator#25]
Not sure the intention is to support ESP32 at some point. Ongoing work to create PCB for this project has both the Arudino Nano and the ESP32.

Tried to compile for ESP32 and got:
`'byte alarm' redeclared as different kind of symbol`

There has also been ongoing discussion to structure the code differently.
A simple solution would be to place alarm in a struct. 
Tried to look into the variable collision really fast but could not identify it.
A simple renaming would also work.

Not sure which way to go so I didn't create a PR for this.

**Comment by ermtl** [comment]
@frippe75 alarm has been renamed alarmNum to avoid a reserved name. Does it solve the issue ?

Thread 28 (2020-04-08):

### ISSUE TITLE
Using potentiometers for PEEP, TIDAL_VOL, and RESP_RATE

### ISSUE THREAD

**Issue by billygts15** [ermtl/Open-Source-Ventilator#28]
I'm trying to get the potentiometers working for the PEEP, TIDAL_VOL, and RESP_RATE, but need a little help defining the pins.

**Comment by ermtl** [comment]
The MIT design uses them, but the risk for accidental moves is important and they needed to add a confirmation button, so that might not be as easy and intuitive to use as it seems.  If you want to add them, you can use pins A0,A2,A3 for the 3 potentiometers as they are currently unused. 
You can read them at the same place as analogReadKeys();
When they are moved, you can change menuItem so that the right item is displayed then call setDisplayMenu. If you add that and want it merged, please make sure the changes use conditional compilation so that the option can be activated or not.

**Comment by billygts15** [comment]
Thanks.

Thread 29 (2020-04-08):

ermtl/Open-Source-Ventilator #29: Additional hardware options ( like the ones  in MIT E-Vent  )

GoDotMad, 2020-04-08:
I tried using this firmware but the required display and keys are not available here.
I know we could use the serial interface 
but it is not very intuitive. 
therefore can you add the hardware specified in MIT website? 
I tried doing that but I couldn't run the code using a test stepper while not connected to the machine 
it seams never executing the stepper.MoveTo(motorTarget) 
or it could be that I don't understand how it is ment to work.
one last thing why your need humidity and temperature readings ?
I'm planing to use mpx5050 pressure sensor 
and without patient mode

ermtl, 2020-04-08:
The display and the stepper control are independent, so this should not be the issue. 
Someone else (Billybrun) seems to be working on adding MIT style potentiometers. 
https://github.com/ermtl/Open-Source-Ventilator/issues/28
To start the ventilation process (motor), from the serial interface, you need to type the "1" command.

Here are all the serial commands:
                        "0 Stop assisted breathing\n"
                        "1 Start assisted breathing\n"
                        "CV sets Constant Volume mode\n"
                        "CP sets Constant Pressure mode\n"
                        "S set Speed (in BPM)\n"
                        "V set Volume (in ml)\n"
                        "P set Pressure (in cm H2O)\n"
                        "E set PEEP (in cm H2O)\n"
                        "A set Apnea alarm (in cycles)\n"
                        "X set eXpiration ratio (x inspiration)\n"
                        "Y set sYnc (in % of cycle)\n"
                        "M show Measurements from the sensor\n"
                        "T toggle Telemetry data on/off\n"
                        "W Write parameters to permanent memory\n"

Also, MPX5050 seems like a good choice.  If you add that and want it merged, please make sure the changes use conditional compilation so that the option can be activated or not.

Assisted breathing is disabled if the sync period is set to 0 (the respirator will trigger cycles at the programmed BPM without waiting for the patient to initiate a breathing cycle). Normally, both modes are important, but if you want to remove it, the  parameter ee.syncRatio should be set to 0

Humidity and temperature readings were designed as the sensor was originally supposed to be directly in the breathing path where they could be used for several purposes, including an alarm if the tube is not connected correctly to the patient, but since patient secretions would damage the sensor and bringing electrical devices in direct contact with the patient, this would have considerably complicated electrical safety rules and machine cost, so it should be moved in the control box and connected using a sensor tube (just like commercial ventilators). At this location, temperature and humidity are quite useless. The code is still there in case this is needed, but might become a conditional compilation.

GoDotMad, 2020-04-08:
thanks for the reply.
I figured the problem and although I thought it can't  happen to me anymore but here we are.
I connected the step to the direction of the stepper driver.

as for the potentiometers we too think that they are not suitable therefore we will replace them with a mechanical encoder and for the menus I suggest using https://github.com/neu-rah/ArduinoMenu library 

and once I feel I did a good job implementing that changes  to your already great code I will definitely make my first pull request.

closed 2020-04-08 by GoDotMad

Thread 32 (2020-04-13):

### ISSUE TITLE
Use symbolic constants for breathing phases

### ISSUE THREAD

**Issue by grifarais** [ermtl/Open-Source-Ventilator#32]
It would help to understand the code if the different values assigned to breathPhase were defined as symbolic constants or enum. I can generate a pull request if required. Here's how I've understood the code:
typedef enum {
  PHASE_START = 0,
  PHASE_INSPIRATION = 1,
  PHASE_EXPIRATION = 2,
  PHASE_SYNC = 3,
  PHASE_END = 4
} breathPhase_t;

**Comment by ermtl** [comment]
Hi, a major new version is coming, and will have this:

`#define breathPhaseStart           0     // In this phase, all the data for the next breathing cycle are calculated

#define breathPhasePlanedBreathIn  1     // In this phase the motor movement starts  with the programmed values for as long as the planned pressure is not reached

#define breathPhaseStartBreathOut  2     // In this phase, the breath out is calculated and started

#define breathPhasePlanedBreathOut 3     // In this phase the motor movement starts  with the programmed values for as long as the motor position is above 0

#define breathPhasePatientTrigger  4     // In this phase, the patient has inspired (rapid pressure drop)) thus starting a new assisted cycle `

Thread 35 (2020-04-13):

ermtl/Open-Source-Ventilator #35: Handle millis() rollover to zero

iotleaf, 2020-04-13:
I would check usage of millis() when comparing a previous_time & delay_period.

e.g. This will fail after the millis() timer rolls over to zero.
if ( millis() > previous_time + delay_period ) {}

Better to re-arrange
if ( millis() - previous_time >   delay_period ) {}

See
https://www.norwegiancreations.com/2018/10/arduino-tutorial-avoiding-the-overflow-issue-when-using-millis-and-micros/

grifarais, 2020-04-14:
Agreed. Probably better to use unsigned long type for all these timestamp and interval variables too for clarity.

ermtl, 2020-04-14:
The millis() rollover is addressed in a major new version that will be uploaded later today.
I have converted to unsigned long as suggested.

closed 2020-04-14 by ermtl

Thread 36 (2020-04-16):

ermtl/Open-Source-Ventilator #36: compile fail

erez1977mit, 2020-04-16:
Hello,
I keep getting compilation errors in Arduino IDE (1.8.12) on two different computers (WIn10 & MAC).
The error is the same - exit status 1 - 'stepper' was not declared in this scope (see detailed log below)
Beside very few adaptation of the H.file to my configuration (add/remove //) -the file are originals.
I got this failure on version 0.3.
I downloaded all necessary libraries.
any help will be appericiated.

Error log:

/Users/mac/Documents/Arduino/OpenSourceVentilator/OpenSourceVentilator.ino: In function 'void updateBargraph()':
OpenSourceVentilator:830:14: error: 'stepper' was not declared in this scope
    float vol=stepper.currentPosition()/motorVolumeRatio;
              ^~~~~~~
/Users/mac/Documents/Arduino/OpenSourceVentilator/OpenSourceVentilator.ino:830:14: note: suggested alternative: 'strupr'
    float vol=stepper.currentPosition()/motorVolumeRatio;
              ^~~~~~~
              strupr
/Users/mac/Documents/Arduino/OpenSourceVentilator/OpenSourceVentilator.ino: In function 'void Timer()':
OpenSourceVentilator:1595:51: error: 'stepper' was not declared in this scope
  if ((!stopMove) && (timerLvl<=interruptMaxNest)) stepper.run();
                                                   ^~~~~~~
/Users/mac/Documents/Arduino/OpenSourceVentilator/OpenSourceVentilator.ino:1595:51: note: suggested alternative: 'strupr'
  if ((!stopMove) && (timerLvl<=interruptMaxNest)) stepper.run();
                                                   ^~~~~~~
                                                   strupr
/Users/mac/Documents/Arduino/OpenSourceVentilator/OpenSourceVentilator.ino: In function 'void readSensors()':
OpenSourceVentilator:1793:11: error: 'stepper' was not declared in this scope
      if ((stepper.currentPosition()==0) && !ee.active)  // approximate athmospheric pressure by averaging when the bag is filled and the machine does not run.
           ^~~~~~~
/Users/mac/Documents/Arduino/OpenSourceVentilator/OpenSourceVentilator.ino:1793:11: note: suggested alternative: 'strupr'
      if ((stepper.currentPosition()==0) && !ee.active)  // approximate athmospheric pressure by averaging when the bag is filled and the machine does not run.
           ^~~~~~~
           strupr
/Users/mac/Documents/Arduino/OpenSourceVentilator/OpenSourceVentilator.ino: In function 'void setup()':
OpenSourceVentilator:1982:10: error: 'pin_Stepper_DIR' was not declared in this scope
  pinMode(pin_Stepper_DIR, OUTPUT);
          ^~~~~~~~~~~~~~~
OpenSourceVentilator:1984:10: error: 'pin_Stepper_Step' was not declared in this scope
  pinMode(pin_Stepper_Step, OUTPUT);
          ^~~~~~~~~~~~~~~~
OpenSourceVentilator:1987:10: error: 'pin_Stepper_Disable' was not declared in this scope
  pinMode(pin_Stepper_Disable, OUTPUT);
          ^~~~~~~~~~~~~~~~~~~
/Users/mac/Documents/Arduino/OpenSourceVentilator/OpenSourceVentilator.ino: In function 'void motorFastStop()':
OpenSourceVentilator:2168:2: error: 'stepper' was not declared in this scope
  stepper.setAcceleration(motorMaxAcceleration);
  ^~~~~~~
/Users/mac/Documents/Arduino/OpenSourceVentilator/OpenSourceVentilator.ino:2168:2: note: suggested alternative: 'strupr'
  stepper.setAcceleration(motorMaxAcceleration);
  ^~~~~~~
  strupr
/Users/mac/Documents/Arduino/OpenSourceVentilator/OpenSourceVentilator.ino: In function 'void basicTelemetry(boolean)':
OpenSourceVentilator:2195:45: error: 'stepper' was not declared in this scope
      Serial.print(arduinoPlotterMotorOffset+stepper.currentPosition());
                                             ^~~~~~~
/Users/mac/Documents/Arduino/OpenSourceVentilator/OpenSourceVentilator.ino:2195:45: note: suggested alternative: 'strupr'
      Serial.print(arduinoPlotterMotorOffset+stepper.currentPosition());
                                             ^~~~~~~
                                             strupr
/Users/mac/Documents/Arduino/OpenSourceVentilator/OpenSourceVentilator.ino: In function 'void breathingCycleStart()':
OpenSourceVentilator:2351:2: error: 'stepper' was not declared in this scope
  stepper.setMaxSpeed(i);
  ^~~~~~~
/Users/mac/Documents/Arduino/OpenSourceVentilator/OpenSourceVentilator.ino:2351:2: note: suggested alternative: 'strupr'
  stepper.setMaxSpeed(i);
  ^~~~~~~
  strupr
OpenSourceVentilator:2358:19: error: 'pin_Stepper_Disable' was not declared in this scope
      digitalWrite(pin_Stepper_Disable, LOW);  // activate
                   ^~~~~~~~~~~~~~~~~~~
/Users/mac/Documents/Arduino/OpenSourceVentilator/OpenSourceVentilator.ino: In function 'void breathingInspiration()':
OpenSourceVentilator:2388:12: error: 'stepper' was not declared in this scope
  long cpos=stepper.currentPosition ();
            ^~~~~~~
/Users/mac/Documents/Arduino/OpenSourceVentilator/OpenSourceVentilator.ino:2388:12: note: suggested alternative: 'strupr'
  long cpos=stepper.currentPosition ();
            ^~~~~~~
            strupr
/Users/mac/Documents/Arduino/OpenSourceVentilator/OpenSourceVentilator.ino: In function 'void breathOverpressureAlarm()':
OpenSourceVentilator:2440:8: error: 'stepper' was not declared in this scope
    if (stepper.currentPosition()< stepper.targetPosition ())
        ^~~~~~~
/Users/mac/Documents/Arduino/OpenSourceVentilator/OpenSourceVentilator.ino:2440:8: note: suggested alternative: 'strupr'
    if (stepper.currentPosition()< stepper.targetPosition ())
        ^~~~~~~
        strupr
/Users/mac/Documents/Arduino/OpenSourceVentilator/OpenSourceVentilator.ino: In function 'void breathingExpirationStart()':
OpenSourceVentilator:2463:11: error: 'stepper' was not declared in this scope
    long p=stepper.currentPosition()/motorVolumeRatio;
           ^~~~~~~
/Users/mac/Documents/Arduino/OpenSourceVentilator/OpenSourceVentilator.ino:2463:11: note: suggested alternative: 'strupr'
    long p=stepper.currentPosition()/motorVolumeRatio;
           ^~~~~~~
           strupr
/Users/mac/Documents/Arduino/OpenSourceVentilator/OpenSourceVentilator.ino: In function 'void loop()':
OpenSourceVentilator:2573:21: error: 'pin_Stepper_Disable' was not declared in this scope
        digitalWrite(pin_Stepper_Disable, HIGH);  // Deactivate
                     ^~~~~~~~~~~~~~~~~~~
OpenSourceVentilator:2578:56: error: 'stepper' was not declared in this scope
   if (checkMillis(breathe,breathLength+syncDelay) && ((stepper.currentPosition()>0) || stepper.isRunning())) breathe=millis()-(breathLength+syncDelay+50); // wait for the previous cycle to finish (safety)
                                                        ^~~~~~~
/Users/mac/Documents/Arduino/OpenSourceVentilator/OpenSourceVentilator.ino:2578:56: note: suggested alternative: 'strupr'
   if (checkMillis(breathe,breathLength+syncDelay) && ((stepper.currentPosition()>0) || stepper.isRunning())) breathe=millis()-(breathLength+syncDelay+50); // wait for the previous cycle to finish (safety)
                                                        ^~~~~~~
                                                        strupr
exit status 1
'stepper' was not declared in this scope

GoDotMad, 2020-04-16:
as it says in the comments in the code .
the new version uses modified accelstepper library 

thus you have to replace it with the file in libraries folder of the repository

ermtl, 2020-04-17:
That happens if you compile without #define stepDirMotor as you would then need to replace with another type of actuator, may that be a DC motor or pneumatic solenoids or others.
Note that you can leave it defined and test without connecting the motor if you don't have one

closed 2020-04-17 by ermtl

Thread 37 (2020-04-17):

ermtl/Open-Source-Ventilator #37: is there any position feedback implemented?

GoDotMad, 2020-04-17:
I couldn't see in your demonstration nor inside the code a way for setting the starting position 
or limiting the motor movement other than the number of steps.
so correct me if I'm wrong. 
for example if the power goes off while the bag is compressed how does it go to the starting position in the next operation.

ermtl, 2020-04-17:
I'm currently working on a home 'switch' (but it will be optical, not a real switch as it needs a very long life).
The exact implementation is very dependant on your hardware.
the general idea is that the "switch" would be triggered every time the movement ends. 
If it does not get triggered on time, more pulses are issued, if it gets triggered too early, it stops, and that probably means the motor missed some steps. if the condition happens too often, an alarm should be triggered.

GoDotMad, 2020-04-17:
what about optical encoder as well?

ermtl, 2020-04-17:
it would be nice, but not very useful.
the compressed bag will act like a loaded spring. If the motor start losing steps, it means the pressure is way over what it should normally be or there is a mechanical problem and it will lose a lot of steps, trying to correct for it is almost hopeless and the best course of action is probably just to accept that the cycle is abnormal, detect it and try another cycle. If the problem persists, then alarm as there is not much else to do.
Servo motors/servo stepper controllers (except very expensive ones such as Yaskawa) would require an idle timeout or a system reset to restart after an error, so they are not appropriate.

closed 2020-04-18 by ermtl

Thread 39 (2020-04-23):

ermtl/Open-Source-Ventilator #39: How to determine the required speed and acceleration of the stepper motor?

GoDotMad, 2020-04-23:
your stepper seems like it is rotating multiple times each cycle and you mentioned the it is on microstepping. 
and therefore requires a high speed and acceleration 
so is the modification in accelstepper library that effective? 

my mechanical construction made it that the motor has to move a lot to compress the bag and thats why it skips some steps ( a lot ).

ermtl, 2020-04-24:
I'm modifying the accelstepper library now.
the released version (works with my hardware) is simply sending 2 pulses at a time, I'm working on a better one that also takes less time to execute and offers both higher step pulse speed and smoother operation (less noisy) at low speed.
The speed and acceleration are calculated in the breathingCycleStart function.
the amount of total movement can be changed with motorVolumeRatio and the non linearity can be compensated with the volume2pos function (and the online function calculator)

Many things could make your motor skip steps. I haven't seen your design, but most I have seen are very under powered. a NEMA17 motor will not work, a 3D printer driver won't work either. 12V won't work, 24V is marginal.
My current setup that not only moves, but keeps working under load (up to 60 cm H2O) at max speed (35 BPM) with max volume and 1/3 I/E ratio does a full stroke in 0.4 second and uses a 4NM motor, a LeadShine driver and a 36V 150W power supply.
The motor is this one:
https://www.automationtechnologiesinc.com/products-page/nema-23/kl23h2100-50-8b/
The controller is the DM882S (too big, but that's what I have):
https://www.aliexpress.com/item/32888516648.html
The DM556 (or maybe DM542S) would do:
https://www.aliexpress.com/item/32999575790.html
It must be a real Leadshine driver. cheap 10$ copies won't do.

My design moves about 3 turns. If yours moves a lot more than that, a servo motor will be needed as steppers lose power as their speed increases.

GoDotMad, 2020-04-24:
I know that the speed and acceleration for each cycle are calculated in starhbreathingsycle()

what I ment was the max speed and acceleration and volume to position ratio in motor parameters section of the header file.

as for the motor I'm using nema 23 but it can deliver 1.5 NM because its what available here

and we can't order parts from china or any other place in times before the pandemic let alone now.

thats why I had to make a mechanical kind of gearbox to increase the torque but that resulted in needing a lot of speed. 

so   should I just give up?

ermtl, 2020-04-24:
I have not tried to check the maximum value, all I know is as of now, I'm getting quite close to the maximum for processor use (that's why I am modifying the accelstepper library)
1.5NM is a bit weak. It can work for tests, but, depending on the gearing, there is a risk that it will be either too slow for max settings or not strong enough to work well under pressure.
If you need to go fast, using 48V might help.
Please note that my double pulse trick only works as long as the motor controller is at least set to half step. if it's already set to full step, doing 2 full steps at once won't work.
I don't know where you can get a stepper motor locally. Maybe find an industrial machine manufacturer or repair shop and ask them to sell you one or where they get their steppers/controllers.

closed 2020-04-24 by GoDotMad

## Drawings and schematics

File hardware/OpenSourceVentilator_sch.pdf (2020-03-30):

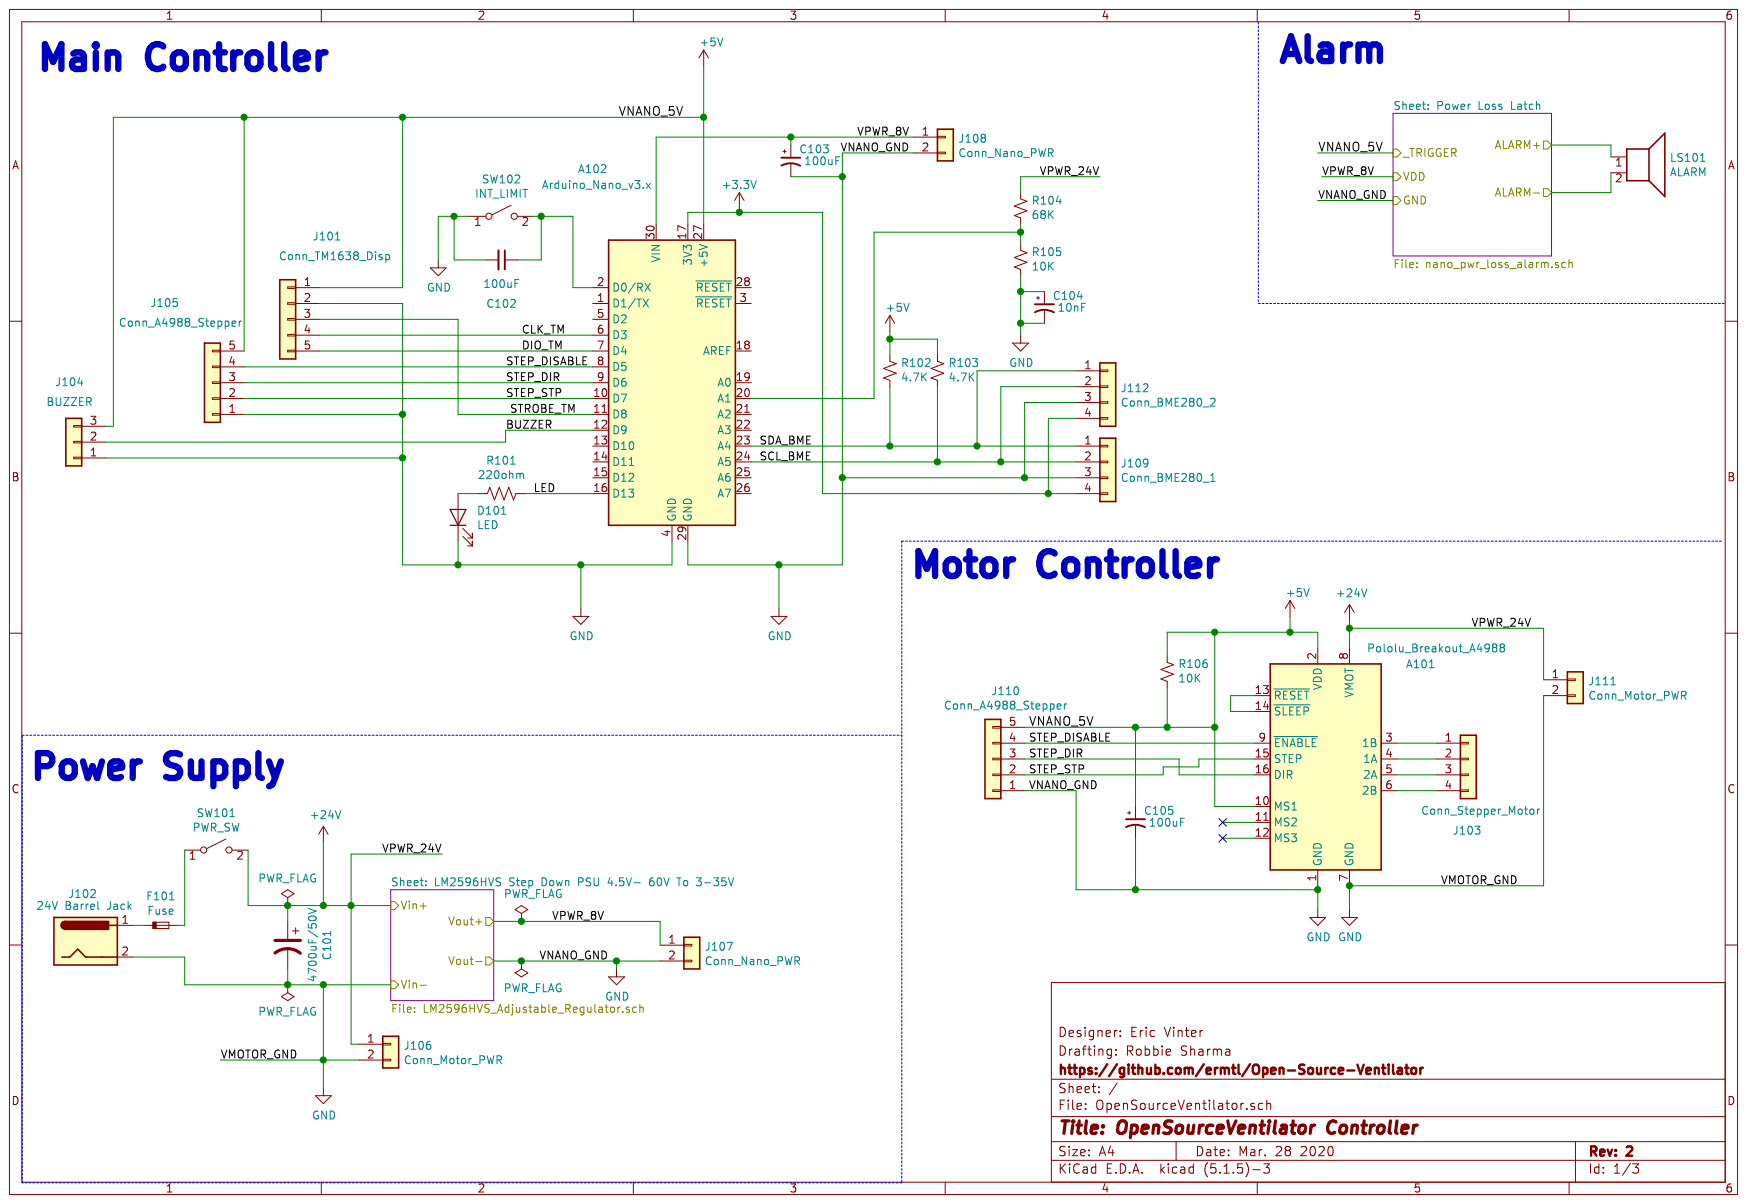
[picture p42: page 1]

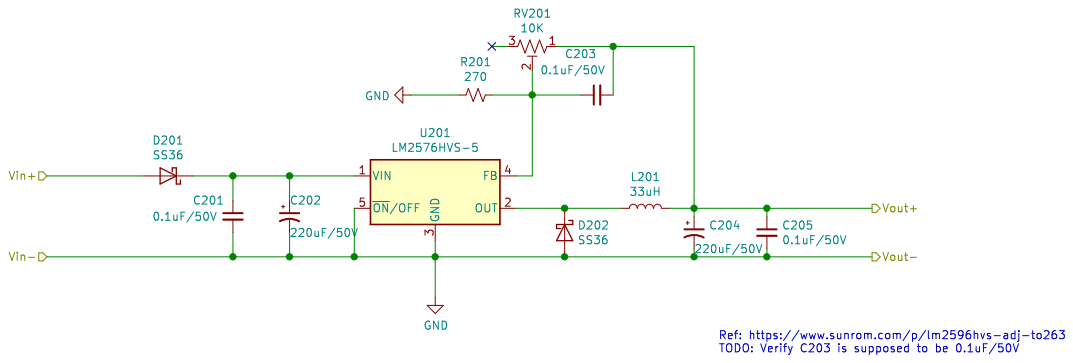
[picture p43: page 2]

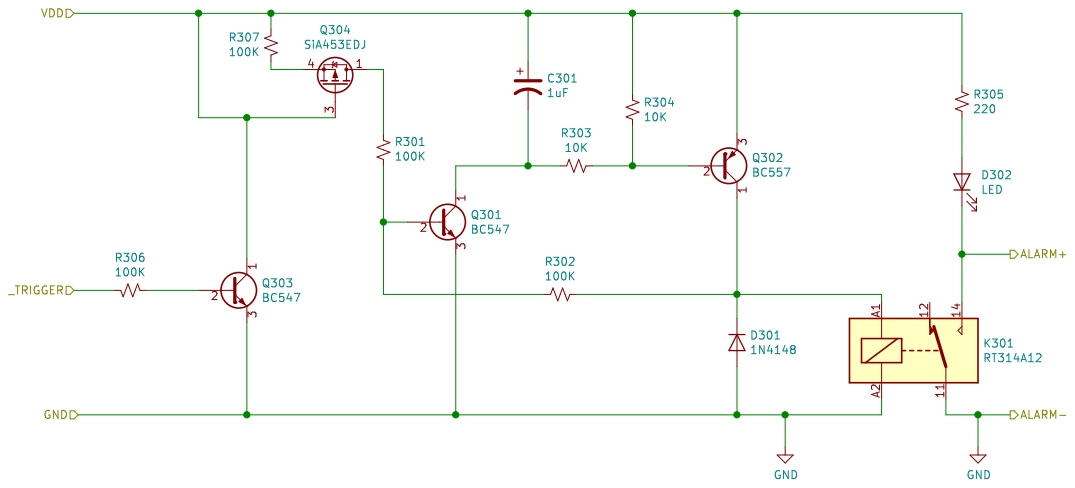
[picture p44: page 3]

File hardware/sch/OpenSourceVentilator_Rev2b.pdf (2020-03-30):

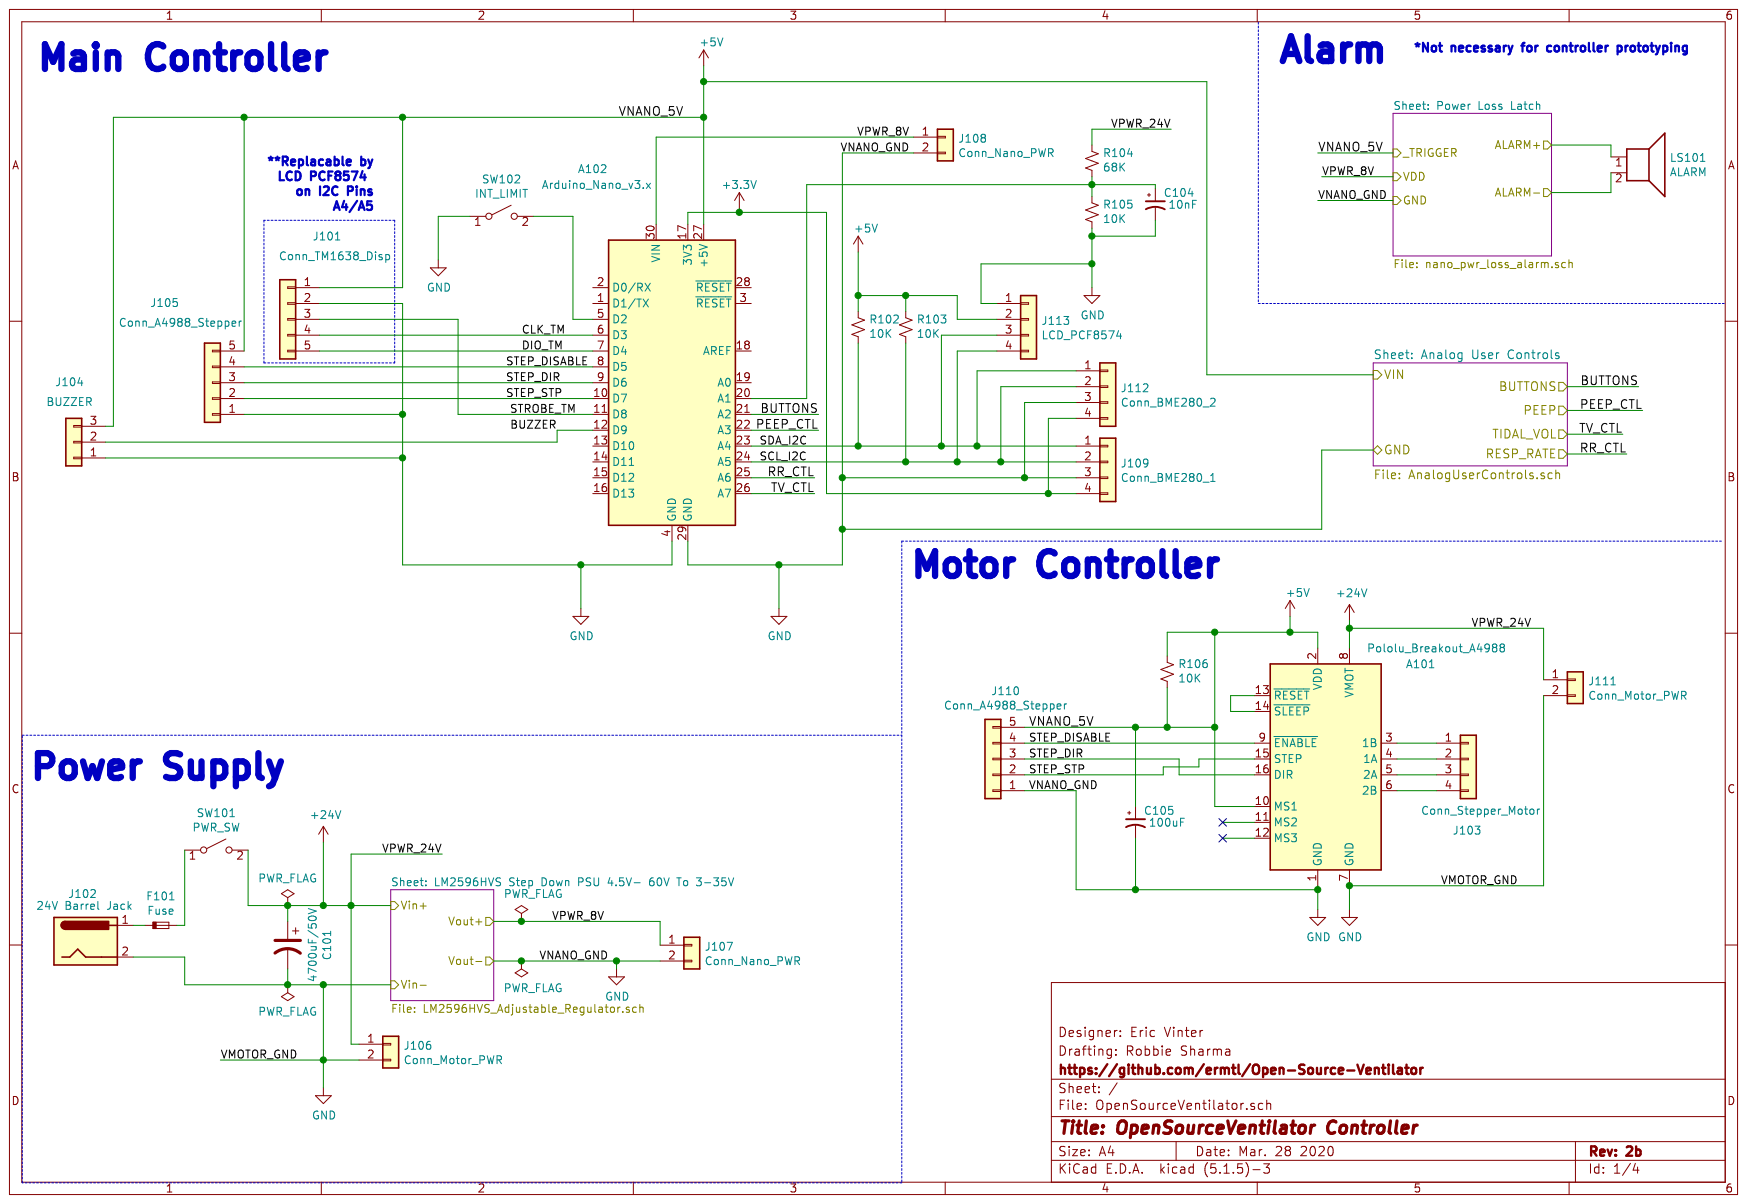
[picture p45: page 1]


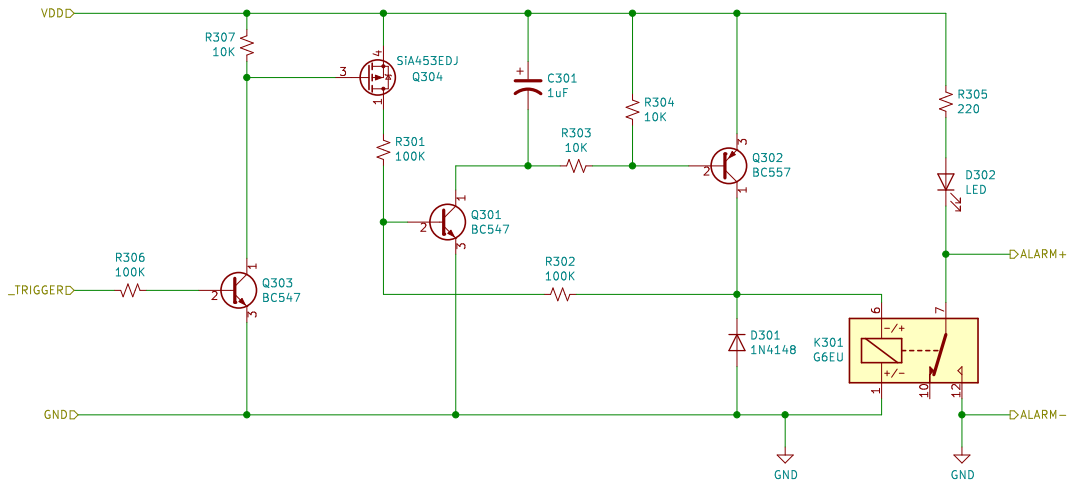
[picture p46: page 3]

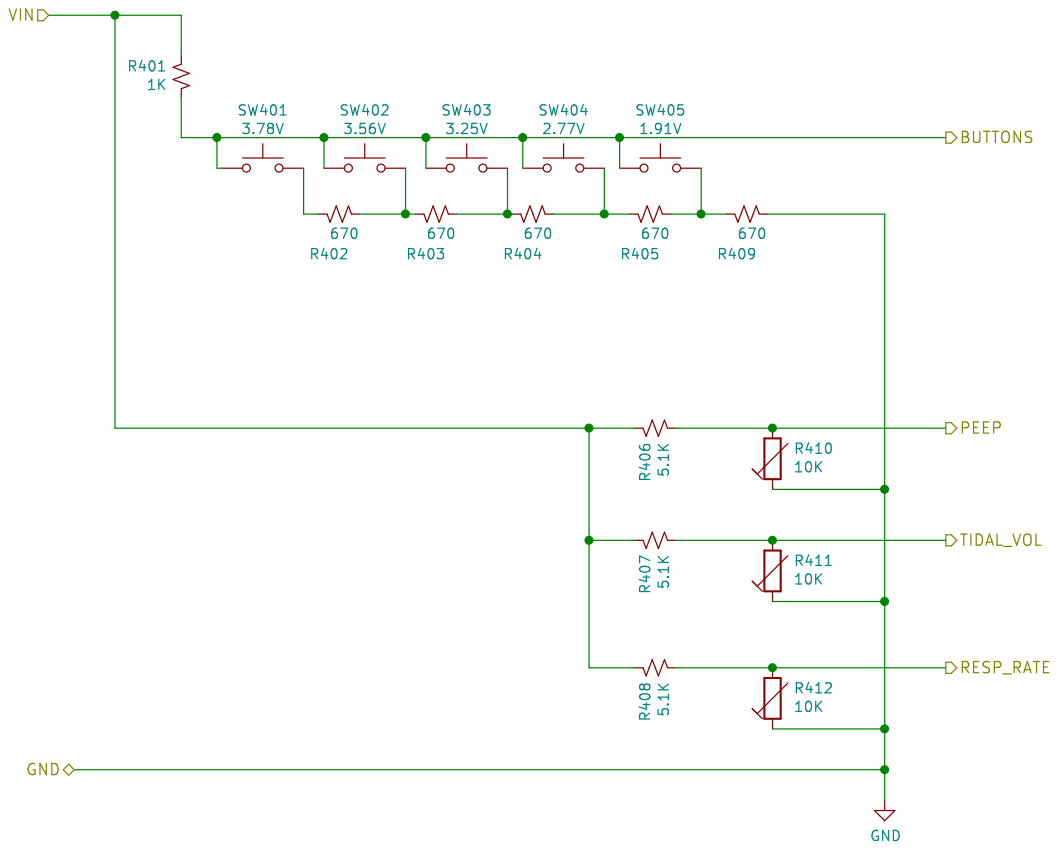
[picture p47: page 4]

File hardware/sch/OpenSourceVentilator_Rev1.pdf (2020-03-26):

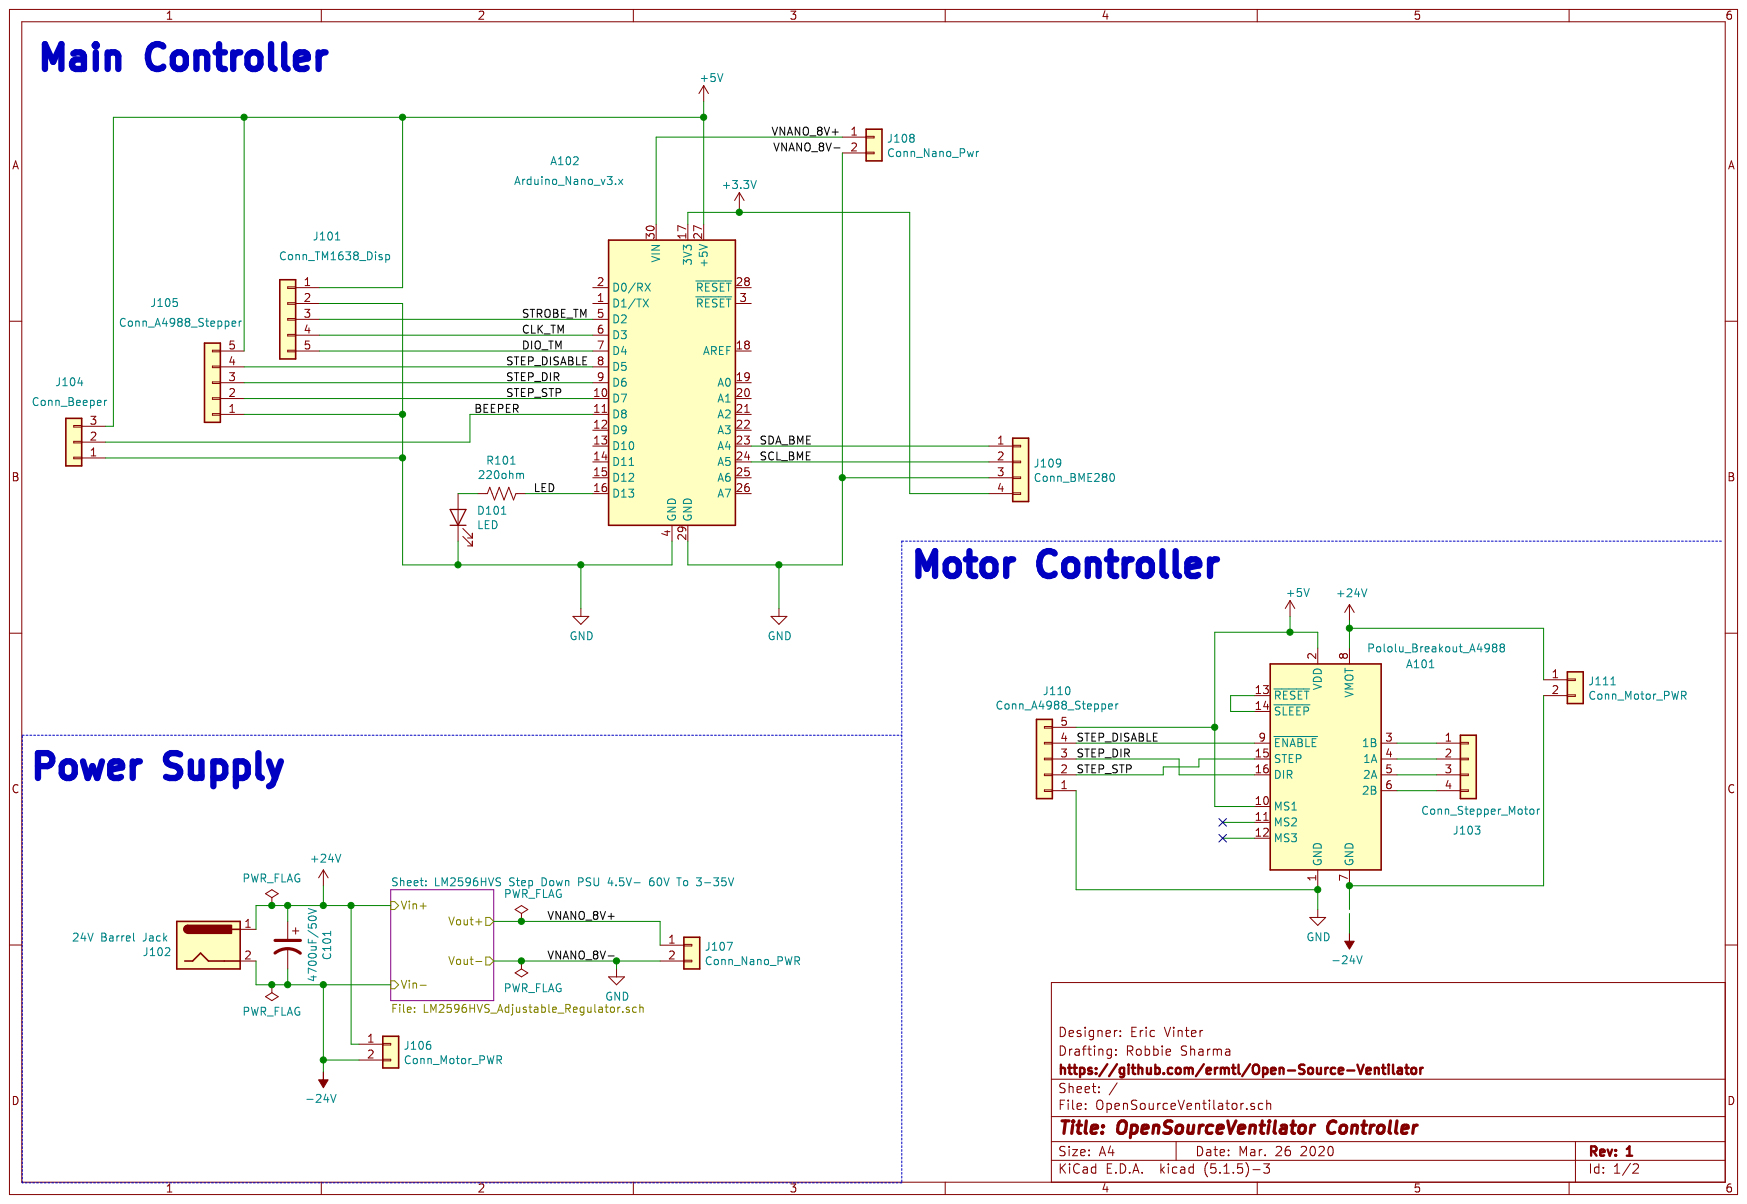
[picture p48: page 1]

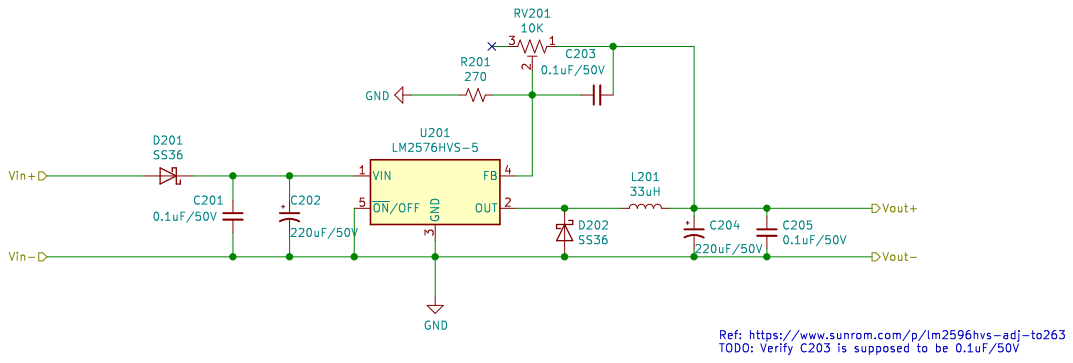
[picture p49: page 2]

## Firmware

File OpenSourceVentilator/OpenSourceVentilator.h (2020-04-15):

/*

  Open source Ventilator

  This file contains OEM parameters for the Open Source Ventilator

  GPL V3 Licence
    --------------
             
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
  Author: Eric Vinter.
  Created March 19, 2020
  EMAIL : erv at mailpeers dot net
  
*/

//************************   DEVICE OPERATIONAL PARAMETERS   ************************  

/*
       WARNING : When changing min and max value, manually change the text in the SerialCommand procedure accordingly

       The values are taken from various documents including :
       https://www.gov.uk/government/publications/coronavirus-covid-19-ventilator-supply-specification/rapidly-manufactured-ventilator-system-specification
       https://docs.google.com/document/d/1h77FkKXqPOwVqfOj-PIJSjYX9QiEx69Av2gYuzqZolw/edit#

       some changes have been made to havee a lower default volume in case the machine is used 
       with an infant to prevent damaging their lungs with an adult setting.
*/

#define minBPM                     10     // minimum respiratory speed
#define defaultBPM                 20     // default respiratory speed
#define stepBPM                     1     // adjustment step for respiratory speed
#define maxBPM                     35     // maximum respiratory speed
#define minVolume                 100     // minimum respiratory volume in milliliters 
#define defaultVolume             400     // default respiratory volume in milliliters 
#define stepVolume                 20     // adjustment step for respiratory volume in milliliters 
#define maxVolume                1000     // maximum respiratory volume in milliliters 
#define minCompression             10     // minimum compression for the ambu-bag in cm H2O
#define stepCompression             2     // adjustment step for compression for the ambu-bag in cm H2O
#define defaultCompression         20     // default compression for the ambu-bag in cm H2O
#define maxCompression             80     // maximum compression for the ambu-bag in cm H2O
#define minPEEPCompression          0     // minimum post expiration compression for the ambu-bag in cm H2O
#define stepPEEPCompression         1     // adjustment step for post expiration compression for the ambu-bag in cm H2O
#define defaultPEEPCompression      4     // default post expiration compression for the ambu-bag in cm H2O
#define maxPEEPCompression         25     // maximum post expiration compression for the ambu-bag in cm H2O
#define minApnea                    0     // minimum value (no detection, no alarm)
#define stepApnea                   1     // adjustment step for apnea alarm (in breathing cycles)
#define defaultApnea                2     // default apnea alarm
#define maxApnea                    6     // maximum apnea alarm

#define minsyncRatio                0     // minimum portion of the cycle for breath synchronisation
#define stepsyncRatio               5     // adjustment step for portion of the cycle for breath synchronisation
#define defaultsyncRatio           15     // default portion of the cycle for breath synchronisation
#define maxsyncRatio               50     // maximum portion of the cycle for breath synchronisation
#define minExpirationRatio          1.00  // minimum portion of the cycle for breath synchronisation
#define stepExpirationRatio         0.2   // adjustment step for portion of the cycle for breath synchronisation
#define defaultExpirationRatio      1.2   // default portion of the cycle for breath synchronisation
#define maxExpirationRatio          3.00  // maximum portion of the cycle for breath synchronisation
#define failVolumeRatio             0.80  // In CP mode, Alarm if pressure reached before that portion of programmed volume.
#define defaultCVMode               true  // CV mode by default 

#define ambientPressureFilter       0.02  // IIR filtering ratio (lower value produce longer time constant)
#define avgPressureFilter           0.25  // IIR filtering ratio (lower value produce longer time constant)
#define motorTargetFilter           0.28  // IIR filtering ratio (lower value produce longer time constant)
#define motorReboundFilter          0.05  // IIR filtering ratio (lower value produce longer time constant)
#define volumeAverageFilter         0.3   // value used to filter the the averaged volume
#define defaultPressure          1033.22  // Pressure in cm H2O returned when no sensor is found (1 atm)
#define defaultAmbientPressure   1033.22  // assumed ambient pressure in cm H2O returned when no sensor is found (1 atm)
#define defaultHumidity            50     // humidity in % RH returned when no sensor is found
#define defaultTemperature         20.00  // temperature in °C returned when no sensor is found
#define alarmCompressionValue       1.1   // if the pressure exceeds the presed value * alarmCompressionValue, 
                                          // then trigger an alarm and stop the motor if needed  
#define minAtmosphericPressure    583     // minimum atmospheric pressure that would be considered valid (15000 ft / 4577m)                                          
                                          // Source : https://www.avs.org/AVS/files/c7/c7edaedb-95b2-438f-adfb-36de54f87b9e.pdf
#define maxAtmosphericPressure   1200     // maximum atmospheric pressure that would be considered valid                                           


/*******************************   MOTOR PARAMETERS   *******************************
 *    
 *     These values will be highly dependant on mechanical design.
 *     When modifying the values, always check with an oscilloscope that the movements completes    
 *     without overlaps and without too much idle time. 
 *     Also check that the motor can properly follow the speed acceleration required under load.
 *     Wrong values can cause unpredictables moves and motor stalls.
 *     The worst case scenario is at max BPM, with max volume, max sync period and max ratio
 *     With default parameters, the whole compression can become as short as 250 ms
 */

#define motorSpeed               5000     // Speed for 1 liter/second
#define motorAcceleration        8500     // Acceleration for 1 liter / second (inverse square of flow)
#define motorMaxAcceleration    30000     // deceleration when pressure limit reached
#define motorMinAcceleration      100     // minimum acceleration to prevent stalling / very slow moves
#define motorMaxSpeed            4000     // Max steps per second. 
#define minMotorMove                5     // the motor does not move for less than this distance
#define motorVolumeRatio            0.8   // Ratio of distance in steps to air volume in step per milliliter (after linearity correction).
#define StallTimeout              500     // force move if motor not positionned (safety)

#define alarmDuration             300     // Length of the alarm for each error (around 4 seconds) 


/*******************************   HARDWARE OPTIONS   *******************************
 *    
 *    It's normal for the program to not compile if some of these are undefined as they need an alternative
 *    
 */

#define arduinoNano        // defines the board as an Arduino nano with with Atmega328P processor
                           // You can define your own board and pinout.

#define USBcontrol         // USB / serial Command line interface.
                           // This allows complete control of all parameters.

#define E2PROM             // Uses the internal EEPROM for parameter storage

#define analogKeyboard


#define PCF8574LCDDisplay  // Use a 2x16 characters LCD with a PCF8574 'backpack' as a display

#define PCF8574LCDbargraph // Use a 2x16 characters LCD with a PCF8574 'backpack' for the Led pressure bargraph

//#define TM1638Keyboard     // Use a TM1638 for the keyboard

//#define TM1638Display      // Use a TM1638 for the display

//#define TM1638bargraph     // Use a TM1638 for the Led pressure bargraph

#define activeBeeper       // active beeper can be used on any pin. Passive beeper will require a PWM capable pin

#define Led                // Led debugging / Signal (should be disabled if SPI peripherals are present)

#define BoschBMxSensor     // Bosch Sensortech BMP280 or BME280

//#define BoschBMP180Sensor  // Bosch Sensortech BMP180 

//#define TwoPressureSensors // Double pressure sensor (one for barometric pressure)

#define stepDirMotor       // Control the motor with step and Direction signals

#define disableMotorctrl   // control moter activation / desactivation      

//#define CurrentSense     // uncomment to add motor current sensing with the Allegromicro ACS712 sensor
                           // This is not enabled by default as first test show the sensor is not sensitive
                           // enough. Another sensor should probably be used.

// # define watchdog       // WARNING: Do not enable this setting  while debugging, you might brick 
                           // your dev. board. If this happens, you'll need to flash not just the 
                           // bootloader, but the whole program space.
                           // The problem is worse in Nanos with a bootloader that does not clear
                           // the watchdog settings. 

#define serialTelemetry    // Sends real time data about time, current breathing phase, motor position, pressure 
                           // while the machine works in CSV format

//#define rampUp           // The cycle volume will ramp up when the machine start and regulate to prevent overpressure                           
                           // As of now, this is highly unstable, to be revised.  

#define eepromVersion  100 // version 1.00 of the eeprom data structure

//************************************   DEBUGGING   *************************************

// #define debug_0      // print data for each cycle
// #define debug_1      // print data for user triggered cycle    
// #define debug_2      // print data for 1 in 10 measurement cycles
// #define debug_3      // print sensor datadata 
// #define debug_4      // temperature / humidity / pressure 
// #define debug_5      // See all values read from EEPROM 
// #define debug_6      // Display raw and corrected volumes 
#define debug_7       // makes the alarm sound much shorter
//#define debug_8       // makes the alarm sound much shorter

//#define debugAnalogKeyboard   // Display the actual ADC value for the various keys
//#define I2CCheck              // does an I2C bus scan and reports valid addresses. 
#define debugLed              // Interrupt routine debugging
#define ArduinoPlotter        // This will turn on telemetry automatically and disable other debugs 
                              // With this feature on, absolute pressure and motor speeds are scaled.  
#define debugShortEnter       // When stopping the ventilator, Enter needs to be pressed 2 seconds
                              // and an alarm is sounded. Defining debugShortEnter removes it during debugging

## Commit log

2020-03-20 Version 0.11 with interactive USB control
    Add interactive terminal command line complete control (through USB link)
    A minimal device without screen or keyboard is possible with the same software.
2020-03-22 V0.12 add adaptive negative pressure trigger cycle
2020-03-24 0.14 Proper motor timing, CP and CV control modes
2020-03-26 Imported P1A1 sch from OpenLung
    Initial schematic draft for OSV
    Date: Thu Mar 26 12:01:33 2020 -0600
    interactive rebase in progress; onto baf5496
    Last commands done (6 commands done):
    squash 10cded7 Moved schmatics
    squash c8d2bc0 More movements
    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
    [LM2596HVS_Adjustable_Regulator.sch, OpenSourceVentilator.sch]
2020-03-27 V0.15 replacement of buggy Wire.h, Watchdog, misc.
2020-03-28 V0.16Double pressure sensor,modular breath phases
2020-03-29 Added atmega328 datasheet Added arduino datasheet Added pwr jack voltage sense circuit, additional BME280 connector, decoupling caps on nano power input and a4988 power input, changed label refs Adde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
    [LM2596HVS_Adjustable_Regulator.sch, OpenSourceVentilator.sch, nano_pwr_loss_alarm.sch]
2020-03-29 -Moved C104 to junction R104/R105 -Change I2C to 10K resistors -Moved R307 to VDD and G-Q304/C-Q303 junction -Updated K301 relay with G6EU -Remove D101 - LED -Added Analog User Controls (Buttons + PE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
    [AnalogUserControls.sch, LM2596HVS_Adjustable_Regulator.sch, OpenSourceVentilator.sch, nano_pwr_loss_alarm.sch]
2020-03-30 Added sch changes? not sure what
    [OpenSourceVentilator.sch]
2020-03-30 Added UK RMVS Test Data and updated spec document
    [RMVS_TestCaseData.xlsx]
2020-04-01 Front panel for display / buttons / buzzer
    [Panel.FCStd, Panel.stl]
2020-04-02 V0.21 Pressure unit converted to cm H2O / minor changes
2020-04-15 0.3 Complete ventilator release, 3D prints & CNC
2020-04-15 All 3D print STL and CAD files
    [Ambu-Bag 1 support.stl, Ambu-Bag 2 support.stl, Ambu-Bag supports.FCStd, BearingFlange.FCStd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]
2020-04-15 Ventilator wooden box CNC plans
    [Box-1.dxf]
2020-05-10 Foam peep valve (for tests only)
    [Foam Peep 1.stl, Foam Peep 2.stl, Foam Peep 3.stl, Foam Peep Valve.FCStd]

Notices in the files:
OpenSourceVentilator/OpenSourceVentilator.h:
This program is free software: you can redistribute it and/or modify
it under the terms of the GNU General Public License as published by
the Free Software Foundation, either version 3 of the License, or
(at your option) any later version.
